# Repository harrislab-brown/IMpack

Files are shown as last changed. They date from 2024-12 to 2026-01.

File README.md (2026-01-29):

# IMpack

<p align="center">
  
</p>

IMpack is a data logging IMU designed for research applications where sampling rate and compactness are paramount. The board costs less than $100 to fabricate and assemble and features an array of MEMS accelerometer chips which allow it to achieve a maximum acceleration measurement range of +/- 400 g, sampling rates up to 26.6 kHz and an angular rate measurement range of +/- 2000 deg/s. Compared to commercial options that use piezoresistive accelerometer elements and complicated analog frontends, the IMpack is very low cost while still achieving good signal-to-noise ratios via its highly selectable measurement range. The IMpack is 38 mm in diameter and approximately 13 mm thick including the single-cell LiPo battery which powers the device. The mass of the PCB itself is 5 grams; including the specified battery, the mass is 9 grams. The battery can be recharged using the micro USB port and the onboard charging circuitry. The microcontroller (STM32F4) gathers data from 3 high performance MEMS IMU chips and logs data to a micro SD card in a plain text CSV format. The parameters for recording including measurement range and sample rate are adjustable via a plain text settings file on the SD card which is used to configure the device on startup. An I2C expansion port allows the IMpack to interface with external sensors, or the synchronization of an array of IMpacks.

# Capabilities

The IMpack can be configured to sample data using any subset of the chips in its sensor array, including all of them at maximum sampling rate simultaneously. All of the chips used measure acceleration in three axes and the LSM6DSO32 contains a gyroscope as well. Sensor components with different strengths are chosen to improve the versatility of the device to different measurement situations. The MEMS IMU parts used and their primary specifications are listed in the following table.

| Sensor | Sample rate (kHz) | Bandwidth (kHz) | Range | Bit depth |
| :---: | :---: | :---: | :---: | :---: |
| IIS3DWB | 26.6 | 6.3 | +/- 16 g | 16 |
| LSM6DSO32 (accel.) | 6.66 | 3.33 | +/- 32 g | 16 |
| LSM6DSO32 (gyro.) | 6.66 | 1.44 | +/- 2000 deg/s | 16 |
| ADXL373 | 5.12 | 2.56 | +/- 400 g | 12 |

The frequency responses of each of 10 IMpack test units are shown in the plots below for data gathered from each IMU chip on the PCB. More details regarding the test setup are available in the accompanying publication (pre-print in the article directory). The raw testing data are available in the data directory.

<p align="center">
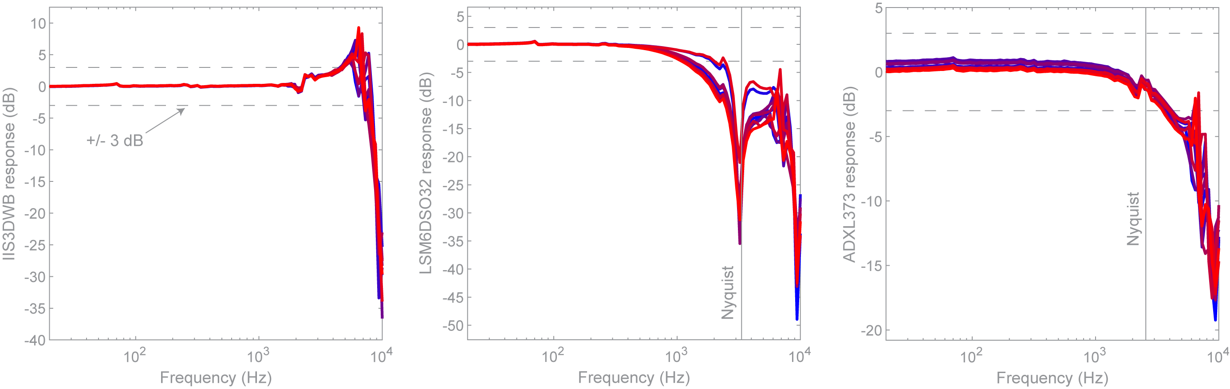
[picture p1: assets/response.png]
  
</p>

# Bill of materials

| Description | Specification |
| :---: | :---: |
| Assembled IMpack PCB |  |
| Mounting fixture or enclosure | Examples in mechanical directory |
| Mounting screws | 4x M2 or #2 cap screws |
| Micro SD card | SanDisk Industrial 8 GB |
| LiPo battery | TinyCircuits ASR00003 |
| Adhesive rubber battery padding | McMaster-Carr 1374N13 |
| Programming cable | Tag-Connect TC2030 |
| Programmer | STLINK-V3MINIE |

# Instructions for use

<p align="center">
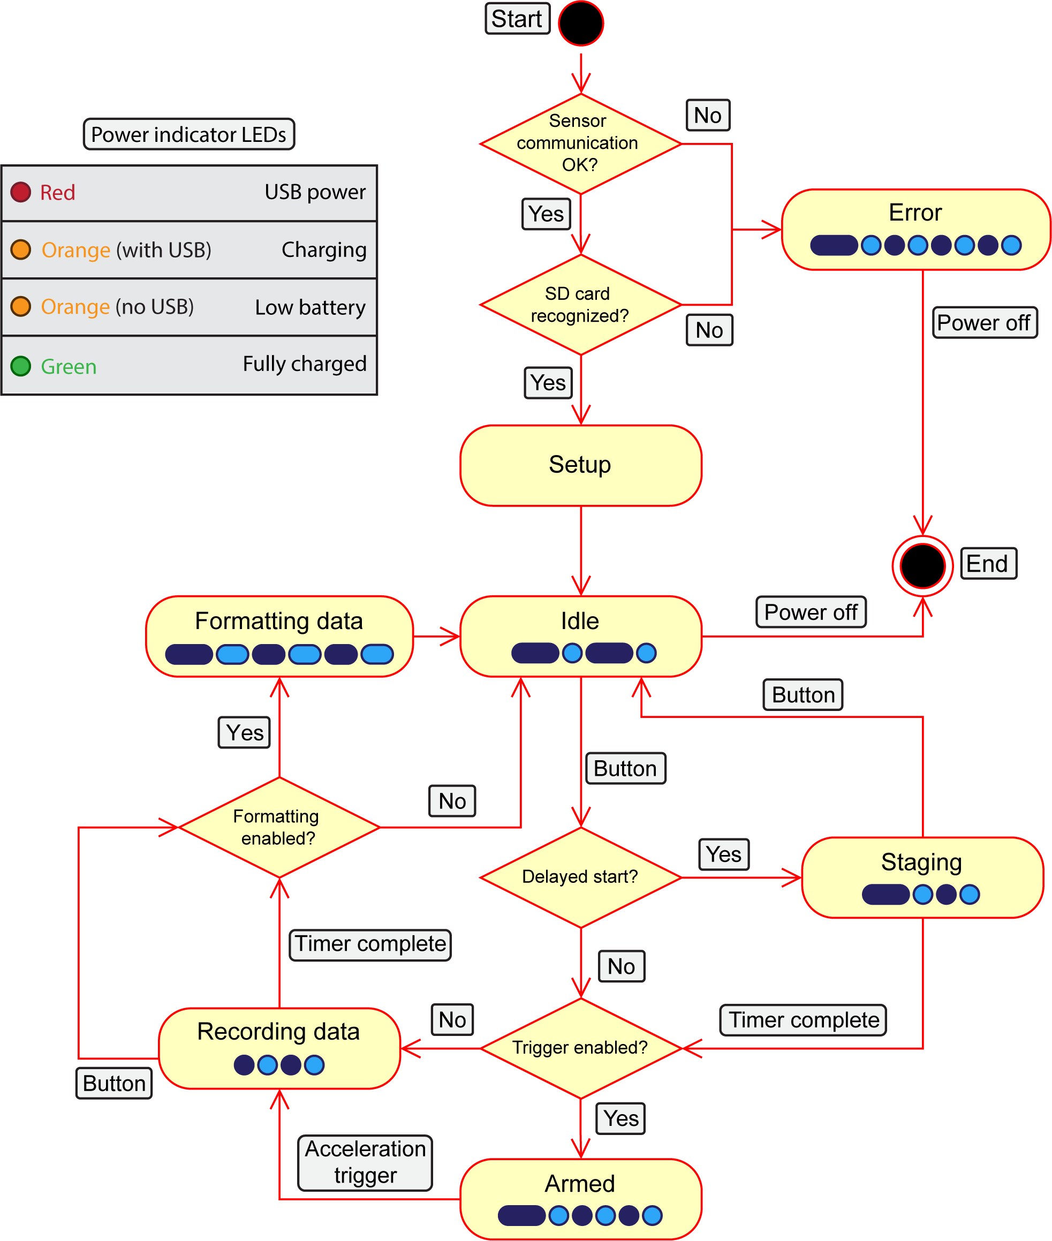
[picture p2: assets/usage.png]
  
</p>

This diagram illustrates the flow of operation of the IMpack. The red, orange and green LEDs are power indicators. The blue LED indicates the state of the device via its periodic blink sequence, where the width of each marker in the diagram indicates the duration of the blink and the light blue color indicates the LED is on. Once the device is powered up and initializes using the settings file on the SD card, pressing the button will begin and end a recording. Recordings can have a delayed start or acceleration trigger, or can stop after a predefined amount of time depending on the configuration as discussed in more detail later.   

## Programming the board

The IMpack is programmed via Serial Wire Debug using an [STLINK-V3MINIE](https://www.mouser.com/ProductDetail/STMicroelectronics/STLINK-V3MINIE?qs=MyNHzdoqoQKcLQe5Jawcgw%3D%3D&mgh=1&utm_id=17222215321&gad_source=1&gclid=Cj0KCQiA3sq6BhD2ARIsAJ8MRwUawTum9u1zJQP-2fxdKjuHkomzrG7uCrwYJbI-F8R0_4U0DyUifOMaAq6kEALw_wcB) debugger and a [Tag-Connect TC2030](https://www.tag-connect.com/product/tc2030-ctx-nl-stdc14-for-use-with-stm32-processors-with-stlink-v3) cable and [retaining clip](https://www.tag-connect.com/product/tc2030-retaining-clip-board-3-pack). We use [STM32CubeIDE](https://www.st.com/en/development-tools/stm32cubeide.html) to compile and launch the project. In the case of a failed flashing that results in an unresponsive microcontroller, the "boot" jumper on the top of the IMpack can be shorted at power up to initialize the microcontroller in boot mode and recover it.

## Charging the battery

The IMpack can be powered from any single-cell lithium polymer battery that can provide at least 150 mA of current and support a 100 mA charge rate. The battery connector is 2-pin JST-SH. We use a [150 mAh battery](https://tinycircuits.com/products/lithium-ion-polymer-battery-3-7v-150mah?srsltid=AfmBOopFKh3iH_07LgFVlMNDD-mnGZ0MBEidQ0zw9-TLOAf2Frq8NPOu) which provides approximately 2 hours of operation on a full charge. The battery polarity is indicated with silkscreen markings near the battery connector. Be sure that your battery matches since there seems to be some variation among different manufacturers.

The IMpack battery can be charged using the micro USB port with the power switch in either the on or off position. The red LED indicates that the IMpack is receiving power over USB. The IMpack can optionally be powered over USB only with no need for a battery. The orange and green LEDs indicate the charge status of the battery. While the USB is plugged in, the orange LED indicates that the battery is charging and the green LED turns on once the battery is fully charged. When operating the device without the USB plugged in, the orange LED will turn on once the battery voltage is low and it needs to be recharged.

## SD card

The IMpack logs data and reads in the recording parameters using a micro SD card. We use an [8 GB SanDisk Industrial](https://www.amazon.com/SanDisk-Industrial-MicroSDHC-SDSDQAF3-008G-I-Everything/dp/B085GL89HQ?th=1) card. The card should be formatted as FAT32. The IMpack will operate in the top-level directory of the card so it is recommended to use an empty card without any important data. 

The IMpack will likely work well with a variety of SD cards but an important factor to note is the write latency of the SD card. This specification is often provided as a generous upper bound so it is difficult to compare the real world performance of different SD cards based on their datasheets. If the real world write latency is too large, some IMU data can be lost during recording. In our testing the IMpack with SanDisk Industrial cards data loss is exceedingly rare.

## Taking a recording

With the IMpack connected to a power source (USB, battery or both), flip the power switch to the on position. The microcontroller will initialize the system and attempt to read in the settings file (more on that later). If the initialization is successful, the blue LED will blink twice. If no settings file is provided or the settings file is formatted incorrectly, the blue LED will blink 4 times. In this case the IMpack will write a correctly formatted default settings file to the card which can subsequently be tweaked by the user to configure the device. The blue LED should then begin flashing once every second, indicating that the device is in the idle state and ready to begin a recording. If instead there is a repeating sequence of 4 blinks, then the IMpack is in an error state (commonly due to a missing SD card).  

When the IMpack is idle, press the button to begin a recording. If a delay is configured, the device will enter the setup state where it waits before recording. A repeating sequence of 2 blue blinks indicates that the IMpack is in the setup state. After the configured delay, the device will enter the armed state if the recording is configured to begin based on an acceleration trigger. A repeating sequence of 3 blinks indicates that the IMpack is in the armed state. Once the acceleration trigger is detected, the device will begin recording, as indicated by rapid blinking of the blue LED. The recording will stop either after the configured recording length, or when the user presses the button again. After the recording, if data formatting is enabled, the device will spend some time formatting the raw sensor data into a plain text CSV file. A sequence of 3 slow blinks will indicate this state. Finally the device will return to the idle state at which point a new recording can be started or the device can be powered off. When the IMpack is not in use, the power switch should be in the off position to avoid draining the battery.

The recording sequence can be configured using the settings file and not all of the aforementioned states will necessarily be seen. For instance, if the delay before the armed state is set to zero and acceleration triggering is disabled, the device will immediately enter the recording state and begin logging data once the button is pressed. Similarly, the formatting state with 3 slow blinks will not be seen if data formatting is disabled, which may be desirable for long recordings at high data rates since the formatting can take a long time. In this case, the recording will be a binary file with the raw sensor data.

## Settings file

The settings.txt file on the SD card is used to configure the IMpack at startup. The sampling parameters for each IMU channel can be configured, as well as the overall recording parameters such as whether to wait for an acceleration trigger or whether to perform plain text formatting of the data file. An annotated example of the default settings file is shown below describing each of the parameters and their allowed values. If a valid settings file is not found on startup, the IMpack will generate a default one on the SD card - this is the recommended way to get started with the configuration.

```
LSM6DSx_accel_enabled = 1  # enable or disable each measurement channel with values 1 or 0
LSM6DSx_accel_odr_hz = 6660  # allowed values: 13, 26, 52, 104, 208, 416, 833, 1660, 3330, 6660
LSM6DSx_accel_range_g = 32  # allowed values: 4, 8, 16, 32
LSM6DSx_accel_lpf = 2  # setting for the low pass filter, 2 means bandwidth = ODR / 2 and so on (same meaning for other the other accelerometers), allowed values: 2, 4, 10, 20, 45, 100, 200, 400, 800
LSM6DSx_accel_offset_x_mg = 0  # these are DC offsets in milli-g, signed integer
LSM6DSx_accel_offset_y_mg = 0
LSM6DSx_accel_offset_z_mg = 0

LSM6DSx_gyro_enabled = 1
LSM6DSx_gyro_odr_hz = 6660  # allowed values: 13, 26, 52, 104, 208, 416, 833, 1660, 3330, 6660
LSM6DSx_gyro_range_dps = 2000  # allowed values: 125, 250, 500, 1000, 2000
LSM6DSx_gyro_lpf = 3  # this is the bit value that is put in the chip register, consult table 60 in LSM6DSO32 data sheet, allowed values: 0, 1, 2, 3, 4, 5, 6, 7

IIS3DWB_accel_enabled = 1
IIS3DWB_accel_range_g = 16  # allowed values: 2, 4, 8, 16
IIS3DWB_accel_lpf = 4  # allowed values: 4, 10, 20, 45, 100, 200, 400, 800
IIS3DWB_accel_offset_x_mg = 0
IIS3DWB_accel_offset_y_mg = 0
IIS3DWB_accel_offset_z_mg = 0

ADXL37x_accel_enabled = 1
ADXL37x_accel_odr_hz = 5120  # allowed values: 320, 640, 1280, 2560, 5120
ADXL37x_accel_lpf = 2  # allowed values: 2, 4, 8, 16, 32
ADXL37x_accel_offset_x_mg = 0
ADXL37x_accel_offset_y_mg = 0
ADXL37x_accel_offset_z_mg = 0

delay_before_armed_ms = 0  # how long to remain in the staging state in ms
recording_length_ms = 5000  # how long to record for in ms
data_formatting_enabled = 1  # if enabled, will create CSV files after each recording
accel_trigger_enabled = 0  # once armed, the recording will start based on an acceleration trigger if enabled
accel_trigger_on_any_axis = 0  # trigger if any axis exceeds the threshold if 1, else if 0 looks only for specific axis
accel_trigger_axis = 2  # 0, 1, 2 for x, y, z, axis selection to trigger from
accel_trigger_level_mg = 500  # level of the trigger in units of milli-g
accel_trigger_rising_edge = 0  # select whether to trigger on rising or falling edge
```

## Data format

When plain text data formatting is enabled, the IMpack will create a separate CSV file for each active channel from the recording. The columns for time stamps and axis measurements are labeled with units, so interpreting the file should be straightforward. The binary data files consist of sequences of data points which each consist of 12 bytes. Each data point contains the unsigned 32 bit time stamp in microseconds, 3 axes of signed 16 bit acceleration/angular rate data, and finally unsigned 16 bit data type tag to indicate which channel produced the data. Example scripts for parsing the binary data in MATLAB and Python are provided in the examples directory. 

# Hardware design

<p align="center">
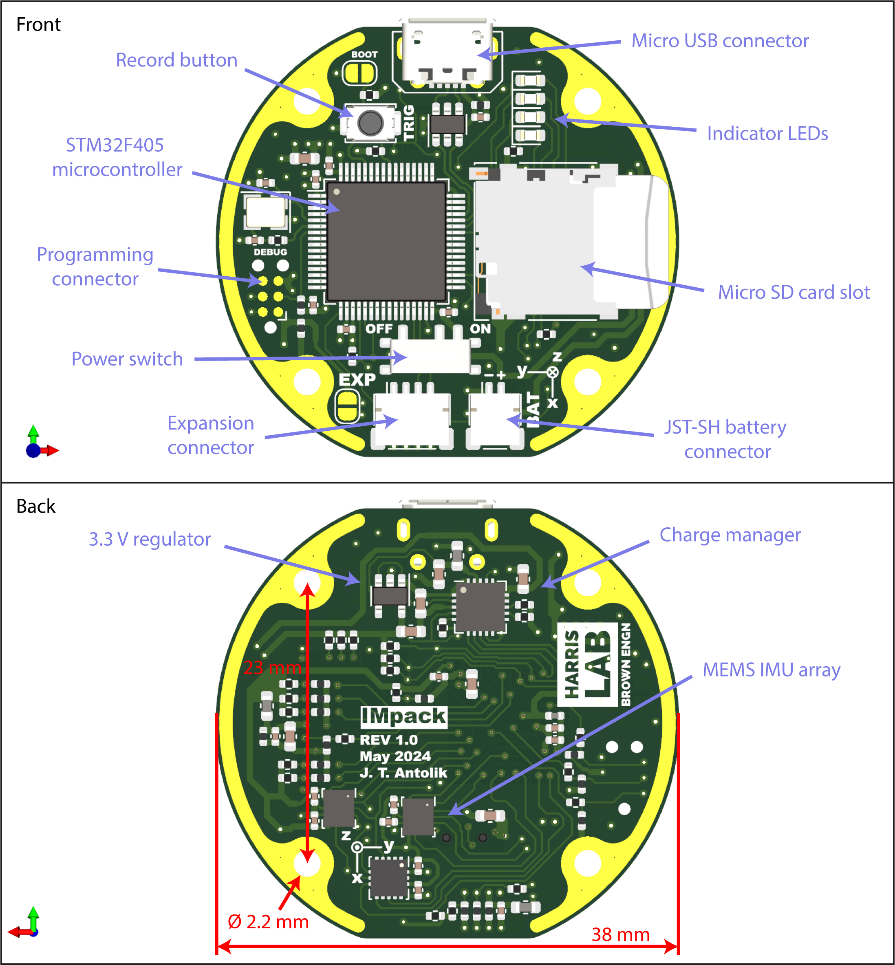
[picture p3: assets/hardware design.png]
  
</p>

The board schematics, production files and KiCad 8 design files are available in the hardware directory. An enclosure or fixture is required to mount the IMpack depending on the application, which could be 3D printed or machined from metal in more stringent testing setups. Design files for the mechanical assemblies into which we mount the IMpack are available in the mechanical directory as examples. In our use case, we apply an adhesive rubber pad to the battery which allows it to be firmly clamped into the battery pocket as the IMpack mounting screws are tightened. The PCB is 4 layers with double sided assembly. The main components and their functions are listed below. A spreadsheet with all of the required components is available under hardware/production.

  - STM32F405 microcontroller (we use SDIO, SPI, NVIC, USB-FS, SWD, I2C hardware)
  - MCP73871 battery charge controller
  - TLV70033 LDO regulator
  - DM3D-SF micro SD card holder (most compact I could find)
  - IIS3DWB super high speed accelerometer with +/- 16 g range
  - ADXL373 high-g range accelerometer
  - LSM6DSO32 combined gyroscope and accelerometer with +/- 32 g range, low cost and widely available fallback option

We ordered 20 fully assembled IMpack units in calendar year 2024 to be manufactured by JLCPCB in batches of 5 or 10. The total cost per board ended up between 60 and 80 USD. A large contributor to the cost is the high performance accelerometer chips IIS3DWB and ADXL373 which typically cost 20 USD per chip in low quanitites. The board could be manufactured with the LSM6DSO32 as the only IMU chip, saving approximately 40 USD per unit, without otherwise compromising the functionality. 

# Firmware design

The source code for the IMpack is available as an STM32CubeIDE project in the firmware directory. The IMpack firmware is written in C and developed using the toolchain provided with STM32CubeIDE version 1.16.0 along with ST's Hardware Abstraction Layer library provided in the STM32Cube FW_F4 V1.28.1 firmware package. The IMpack firmware uses an interrupt based scheme to retrieve data from the IMU chips resulting in minimum latency in which the MCU listens to the data ready pin from each chip and initiates the SPI data read on the appropriate edges of the data pin signal. The SPI read subroutine uses direct register manipulation for improved speed. Each data packet is tagged with a time stamp and an identifier for which chip it came from and inserted into a large double buffer in RAM. The buffer is written to a file on the SD card in binary format periodically as each half of the buffer is filled. Finally, at the end of the recording, the binary data file is read back and converted into a CSV text file on the SD card for more convenient processing by the user. A big challenge is the SD card write latency (up to 250 ms latency according to the data sheet for the SanDisk Industrial card used). Data from the IMU chips needs to be double buffered so we can put new data from the sensors in one half while the other half is being written to the file. This means we would have to store 500 ms worth of data in memory to guarantee no data loss. At such high data rates, this is not feasible without using additional memory chips or a larger MCU. In practice, the actual latency of the SD card we selected is much lower so we don't lose data, but this is something to be aware of if a different SD card is used. Data loss can be easily detected by calculating the interval between successive data point time stamps and comparing with the expected sampling period based on the configuration.

# License

IMpack is licensed under the CC BY-SA 4.0 Creative Commons license.

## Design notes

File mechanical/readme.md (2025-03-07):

## IMpack mechanical designs

This directory contains step files and native Fusion 360 design files for the IMpack itself as well as the fixtures we designed to hold it during testing which can serve as an example for user applications. The shaker mount was used to attach the IMpack to the mechanical shaker for frequency response testing. The threaded mount was used to hold the IMpack in the submerisble water impactor which produced the water entry data. The mounting geometry for the IMpack itself and the battery pocket are the same in both designs and should be replicated in a machined aluminum part if relying on our frequency response data. Note that the IMpack is designed for the plated ring around the outside perimeter of the board's bottom face to act as the mechanical mounting surface. For less sensitive applications or preliminary testing 3D printed parts will likely work fine.

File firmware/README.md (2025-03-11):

# Firmware

This directory contains the STM32CubeIDE project for the IMpack. The project specific header files can be found under firmware/IMpack/Core/Inc and the implementation files under firmware/IMpack/Core/Src. The main application code is contained in app.c following a roughly object-oriented design paradigm where the objects are defined in the corresponding commented header files.

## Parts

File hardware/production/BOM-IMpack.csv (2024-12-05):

Comment | Designator | Footprint | LCSC | Quantity
100R | FB201,FB501,FB701 | L_0603_1608Metric | C1002 | 3
TLV70033_SOT23-5 | U202 | SOT-23-5 | C11337 | 1
16MHz | Y301 | Crystal_SMD_3225-4Pin_3.2x2.5mm | C13738 | 1
10n | C310 | C_0402_1005Metric | C15195 | 1
100n | C302,C304,C306,C307,C308,C312,C401,C502,C601,C602,C603,C604,C605,C606,C701 | C_0402_1005Metric | C1525 | 15
12p | C311,C313 | C_0402_1005Metric | C1547 | 2
STM32F405RGT6 | U301 | LQFP-64_10x10mm_P0.5mm | C15742 | 1
JST_SH_BAT | J201 | JST_SH_SM02B-SRSS-TB_1x02-1MP_P1.00mm_Horizontal | C160402 | 1
JST_SH_EXPANSION | J701 | JST_SH_SM04B-SRSS-TB_1x04-1MP_P1.00mm_Horizontal | C160404 | 1
LSM6DSO32TR | U601 | LGA-14_3x2.5mm_P0.5mm_LayoutBorder3x4y | C1864162 | 1
4u7 | C202,C203,C204 | C_0603_1608Metric | C19666 | 3
10u | C201,C301,C501 | C_0603_1608Metric | C19702 | 3
BUTTON | SW301 | SW_Push_SPST_NO_Alps_SKRK | C202388 | 1
RED | D201 | LED_0603_1608Metric | C2286 | 1
2u2 | C303,C305 | C_0603_1608Metric | C23630 | 2
22 | R305,R306,R307,R501 | R_0402_1005Metric | C25092 | 4
47 | R304 | R_0402_1005Metric | C25118 | 1
510 | R209 | R_0402_1005Metric | C25123 | 1
100k | R202 | R_0402_1005Metric | C25741 | 1
10k | R201,R203,R204,R205,R206,R302,R303,R701,R702 | R_0402_1005Metric | C25744 | 9
47k | R502,R503,R504,R505,R506,R507,R601,R602,R603 | R_0402_1005Metric | C25792 | 9
1k5 | R207,R208,R301 | R_0402_1005Metric | C25867 | 3
39n | L301 | L_0402_1005Metric | C26443 | 1
USBLC6-2SC6 | U401 | SOT-23-6 | C2827654 | 1
SW_ON_OFF | SW201 | MSS12C02LS-BB2.0 | C3008585 | 1
RCLAMP0521P-N | D302,D303,D304,D305,D306,D401,D501,D502,D503,D504,D505,D506,D507,D508,D701,D702,D703 | D_0402_1005Metric | C316043 | 17
ADXL37x | U602 | Analog_LGA-16_3.25x3mm_P0.5mm_LayoutBorder3x5y | C3216386 | 1
USB_B_Micro | J401 | MicroXNJ | C404969 | 1
MCP73871 | U201 | QFN-20-1EP_4x4mm_P0.5mm_EP2.5x2.5mm | C511310 | 1
1u | C309 | C_0402_1005Metric | C52923 | 1
IIS3DWBTR | U603 | LGA-14_3x2.5mm_P0.5mm_LayoutBorder3x4y | C717702 | 1
DM3D-SF | J501 | microSD_HC_Hirose_DM3D-SF | C719027 | 1
GREEN | D203 | LED_0603_1608Metric | C84264 | 1
BLUE | D301 | LED_0603_1608Metric | C84266 | 1
ORANGE | D202 | LED_0603_1608Metric | C84269 | 1

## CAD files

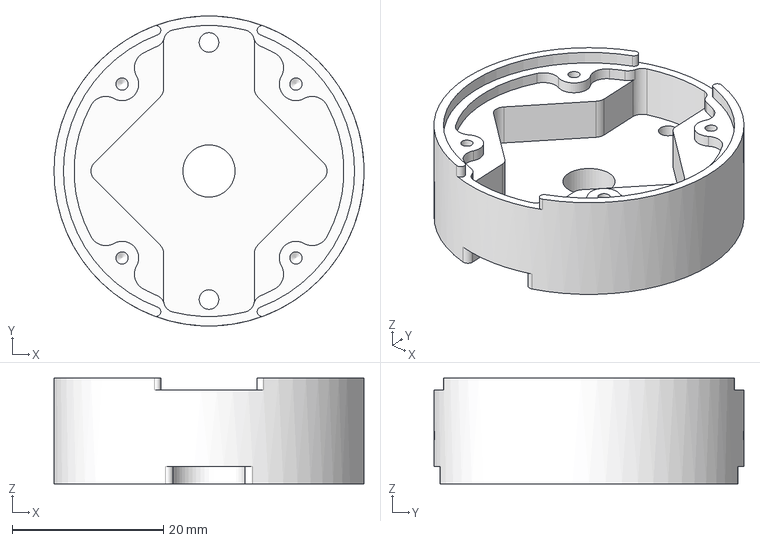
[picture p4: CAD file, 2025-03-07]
mechanical/IMpack shaker mount.step
41.0 x 41.0 x 14.0 mm

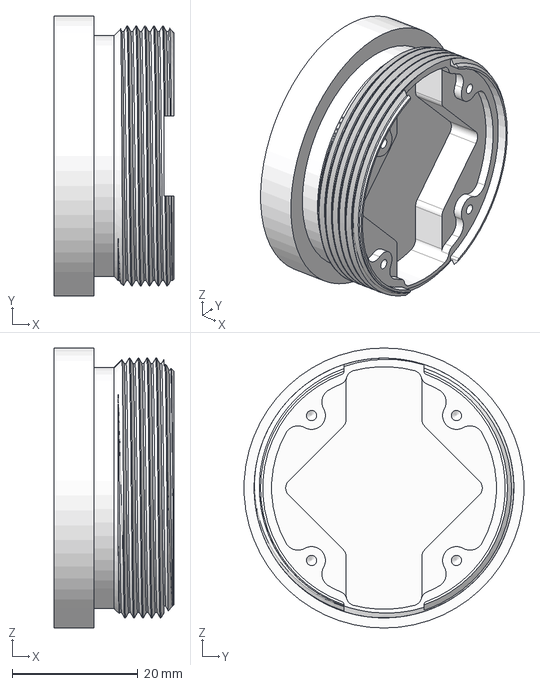
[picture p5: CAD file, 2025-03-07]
mechanical/IMpack threaded mount.step
19.0 x 44.4 x 44.4 mm

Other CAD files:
mechanical/IMpack shaker mount.f3z
mechanical/IMpack threaded mount.f3d

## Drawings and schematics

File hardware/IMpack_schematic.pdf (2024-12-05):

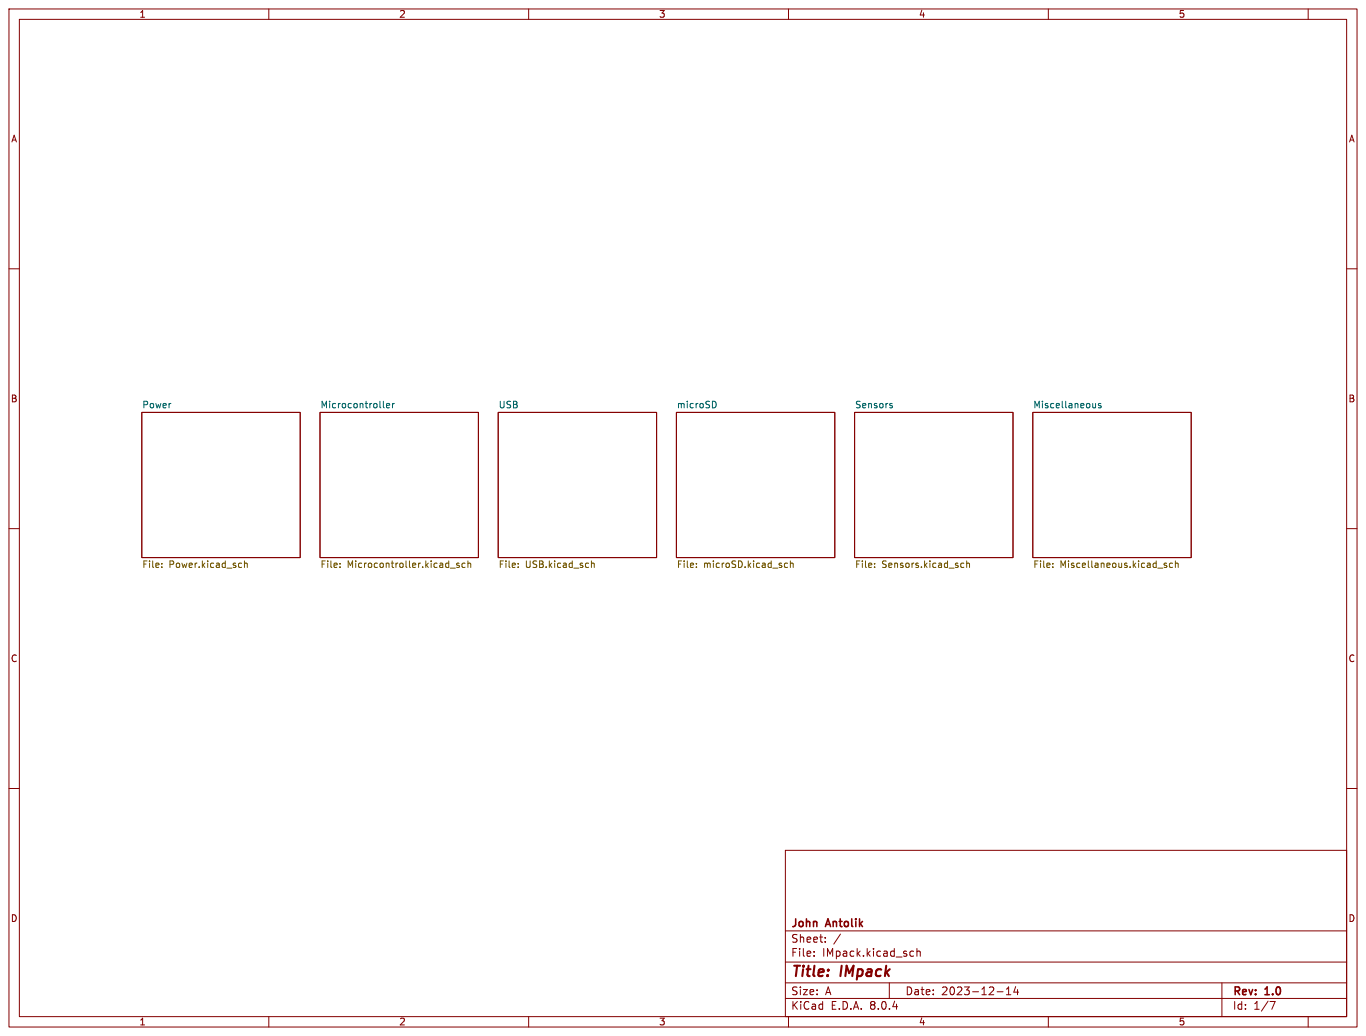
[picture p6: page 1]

File: IMpack.kicad_sch Sheet: / John Antolik

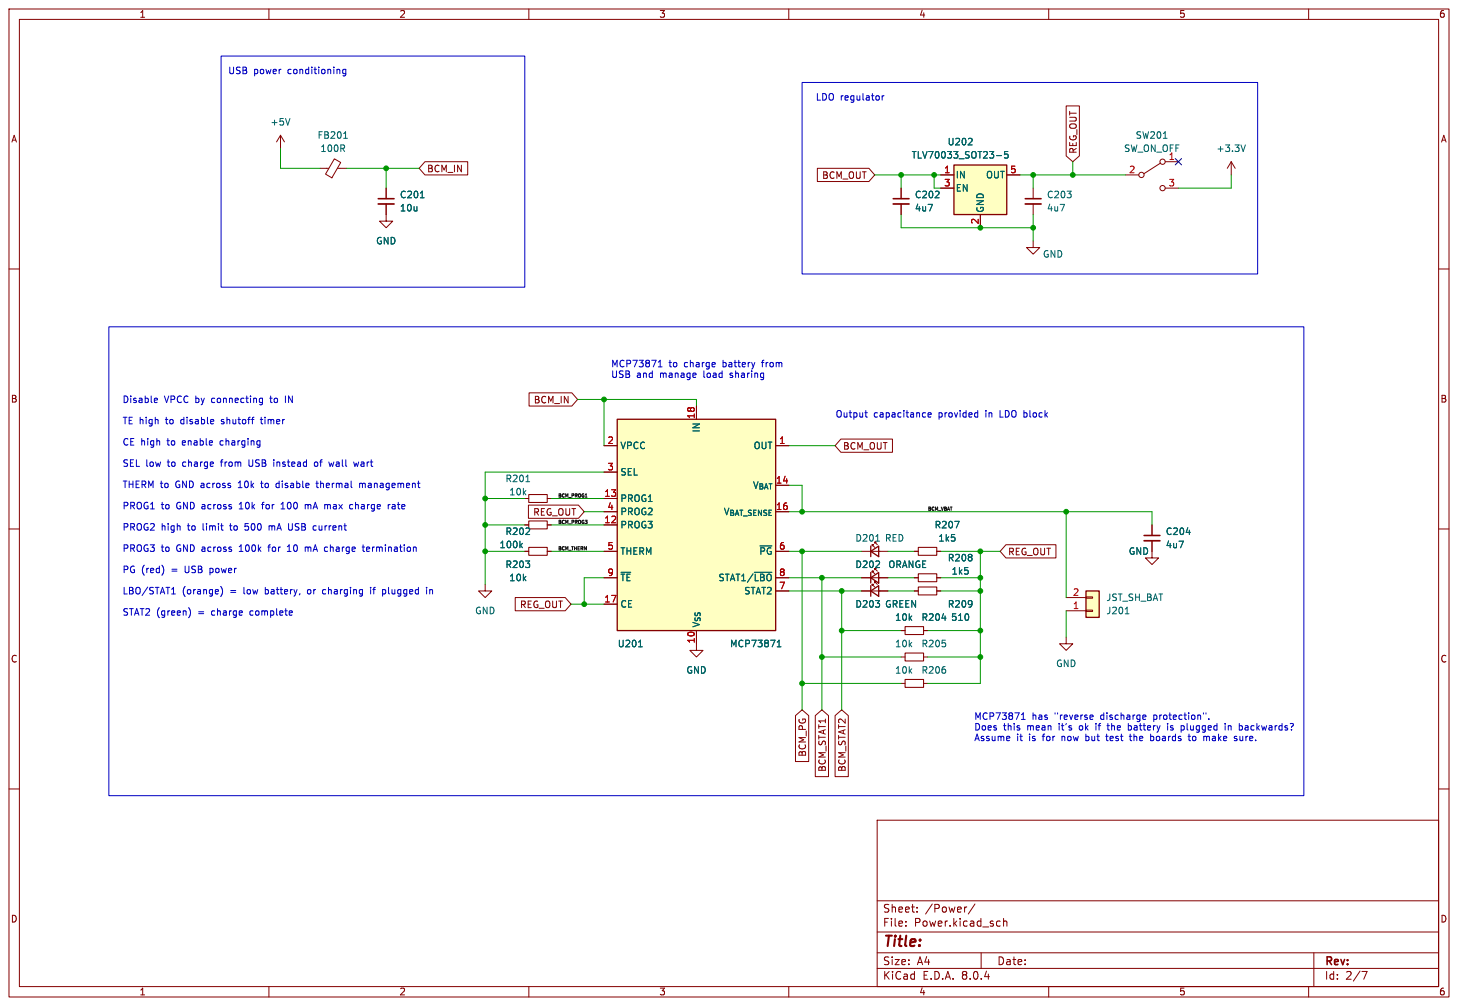
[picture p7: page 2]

Id: 2/7 Title: File: Power.kicad_sch Sheet: /Power/ R208

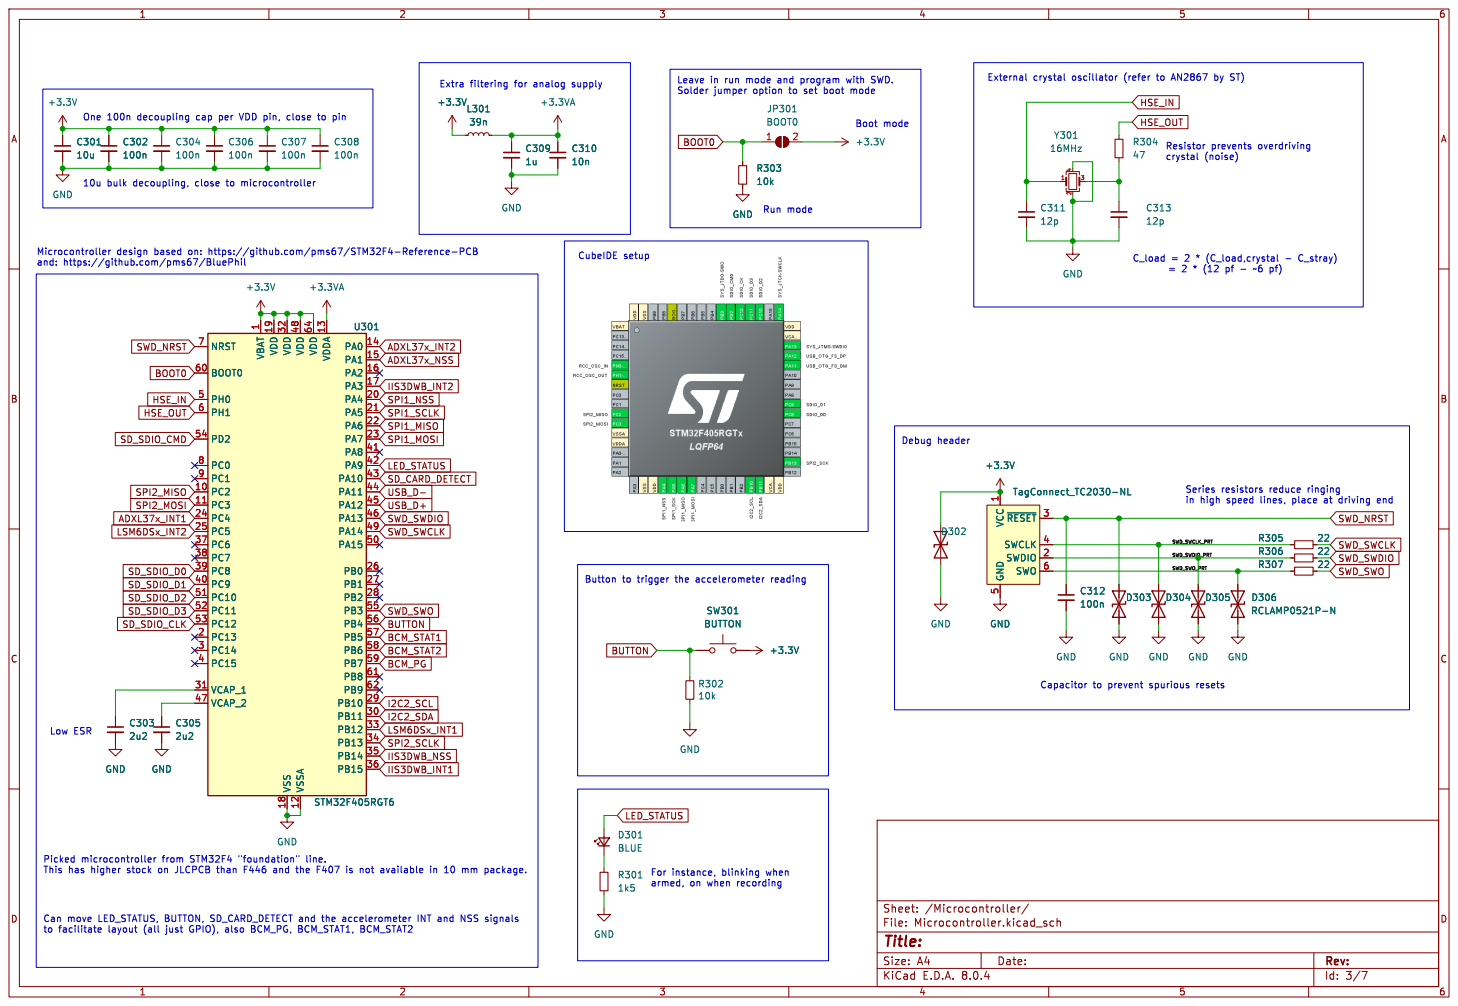
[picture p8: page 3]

1 PC2 10 PC3 11 VSSA 12 VDDA 13 PA0 14 PA1 15 PA2 16 PA3 17 VSS 18 VDD 19 PC13 2 PA4 20 PA5 21 PA6 22 PA7 23 PC4 24 PC5 25 PB0 26 PB1 27 PB2 28 PB10 29 PC14 3 PB11 30 VCAP_1 31 VDD 32 PB12 33 PB13 34 PB14 35 PB15 36 PC6 37 PC7 38 PC8 39 PC15 4 PC9 40 PA8 41 PA9 42 PA10 43 PA11 44 PA12 45 PA13 46 VCAP_2 47 VDD 48 PA14 49 PH0 5 PA15 50 PC10 51 PC11 52 PC12 53 PD2 54 PB3 55 PB4 56 PB5 57 PB6 58 PB7 59 PH1 6 BOOT0 60 PB8 61 PB9 62 VDD 64 NRST 7 PC0 8 PC1 9 U301 STM32F405RGT6 GND GND GND GND

1 PC2 10 PC3 11 VSSA 12 VDDA 13 PA0 14 PA1 15 PA2 16 PA3 17 VSS 18 VDD 19 PC13 2 PA4 20 PA5 21 PA6 22 PA7 23 PC4 24 PC5 25 PB0 26 PB1 27 PB2 28 PB10 29 PC14 3 PB11 30 VCAP_1 31 VDD 32 PB12 33 PB13 34 PB14 35 PB15 36 PC6 37 PC7 38 PC8 39 PC15 4 PC9 40 PA8 41 PA9 42 PA10 43 PA11 44 PA12 45 PA13 46 VCAP_2 47 VDD 48 PA14 49 PH0 5 PA15 50 PC10 51 PC11 52 PC12 53 PD2 54 PB3 55 PB4 56 PB5 57 PB6 58 PB7 59 PH1 6 BOOT0 60 PB8 61 PB9 62 VDD 64 NRST 7 PC0 8 PC1 9 C305

1 SWDIO 2 ~{RESET}3 SWCLK 4 GND

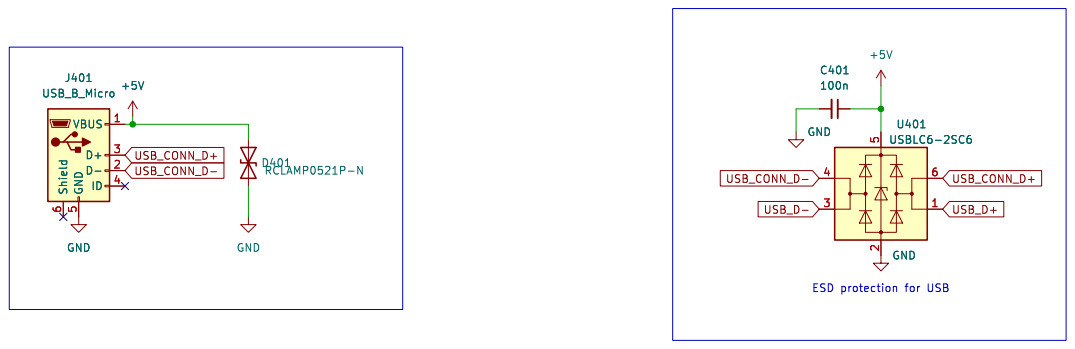
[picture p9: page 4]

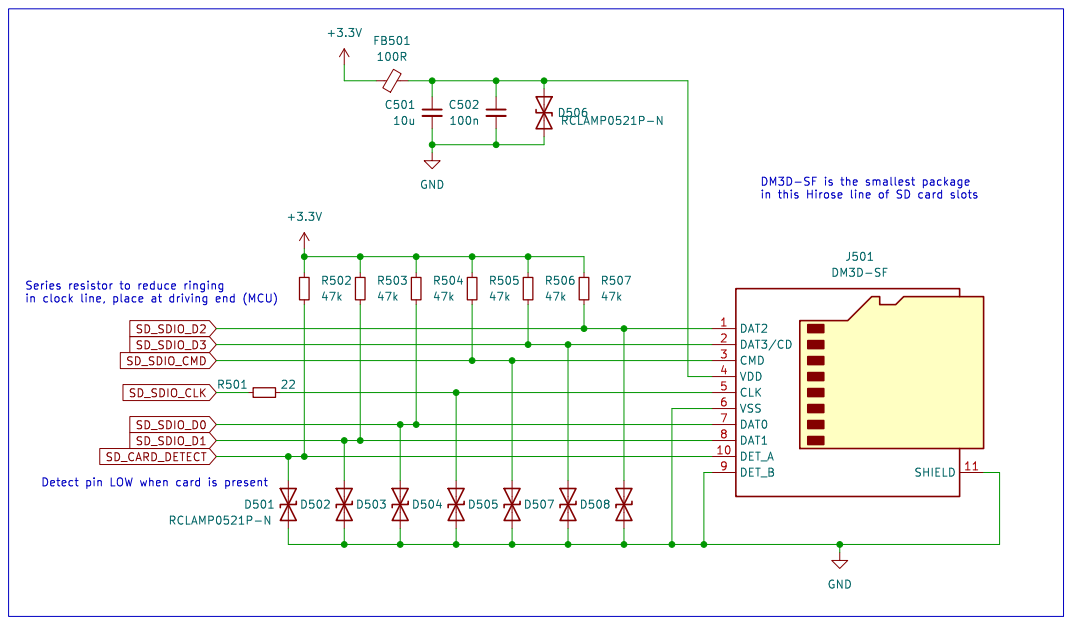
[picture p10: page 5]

in this Hirose line of SD card slots

Id: 5/7 Title: File: microSD.kicad_sch Sheet: /microSD/

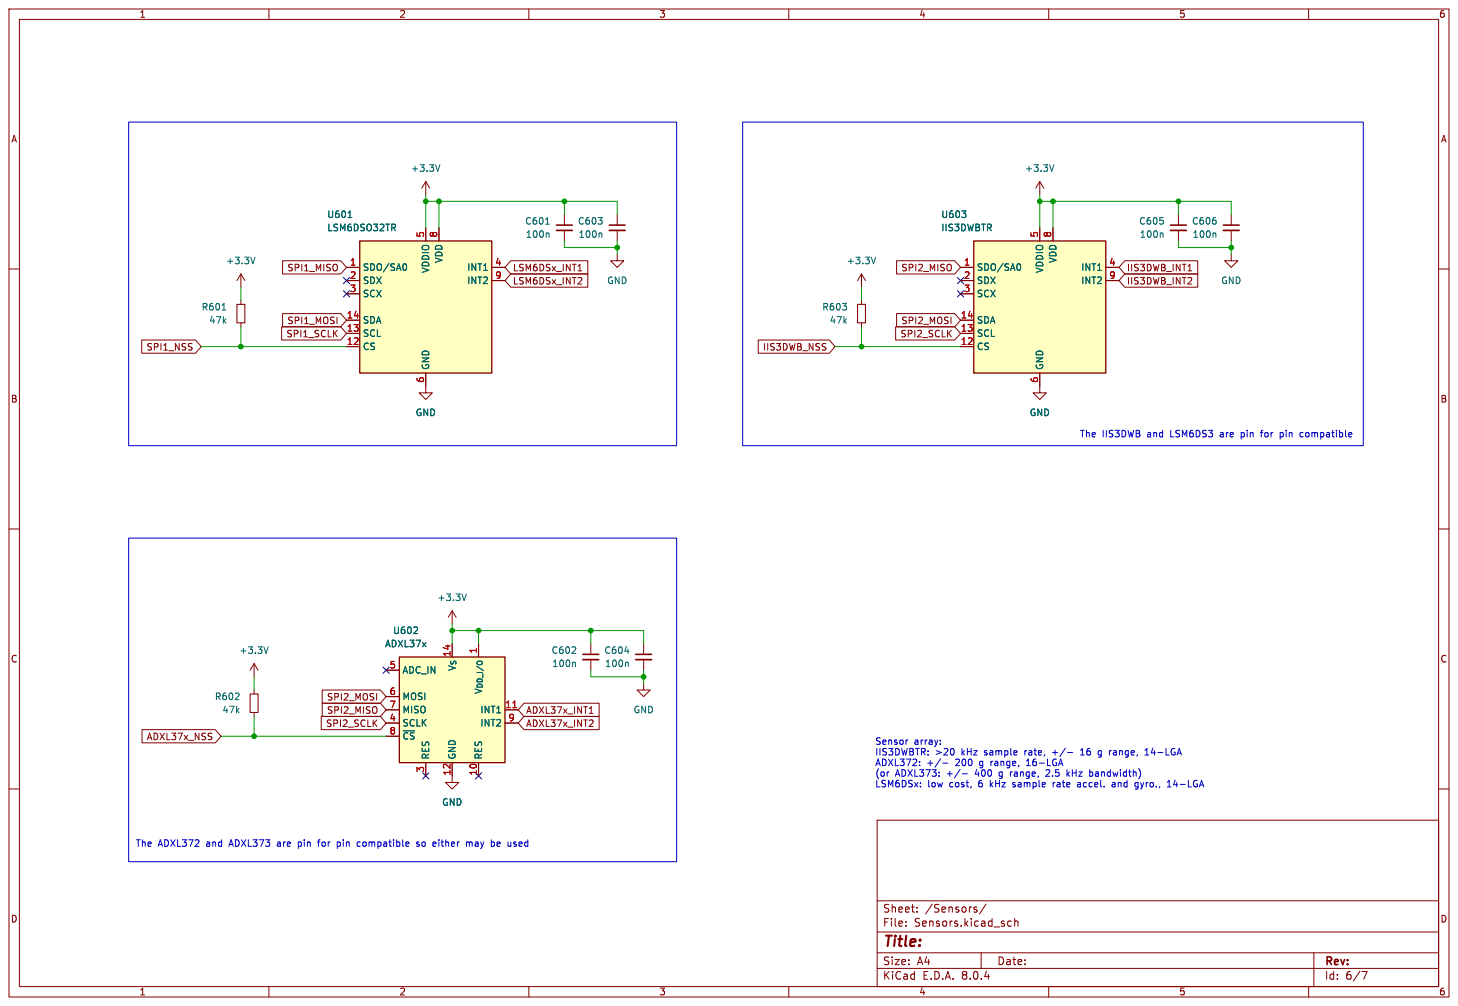
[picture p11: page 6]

The IIS3DWB and LSM6DS3 are pin for pin compatible Sensor array:

3 SCLK 4 ADC_IN 5 MOSI 6 MISO 7 ~{CS} 8

Id: 6/7 Title: File: Sensors.kicad_sch Sheet: /Sensors/

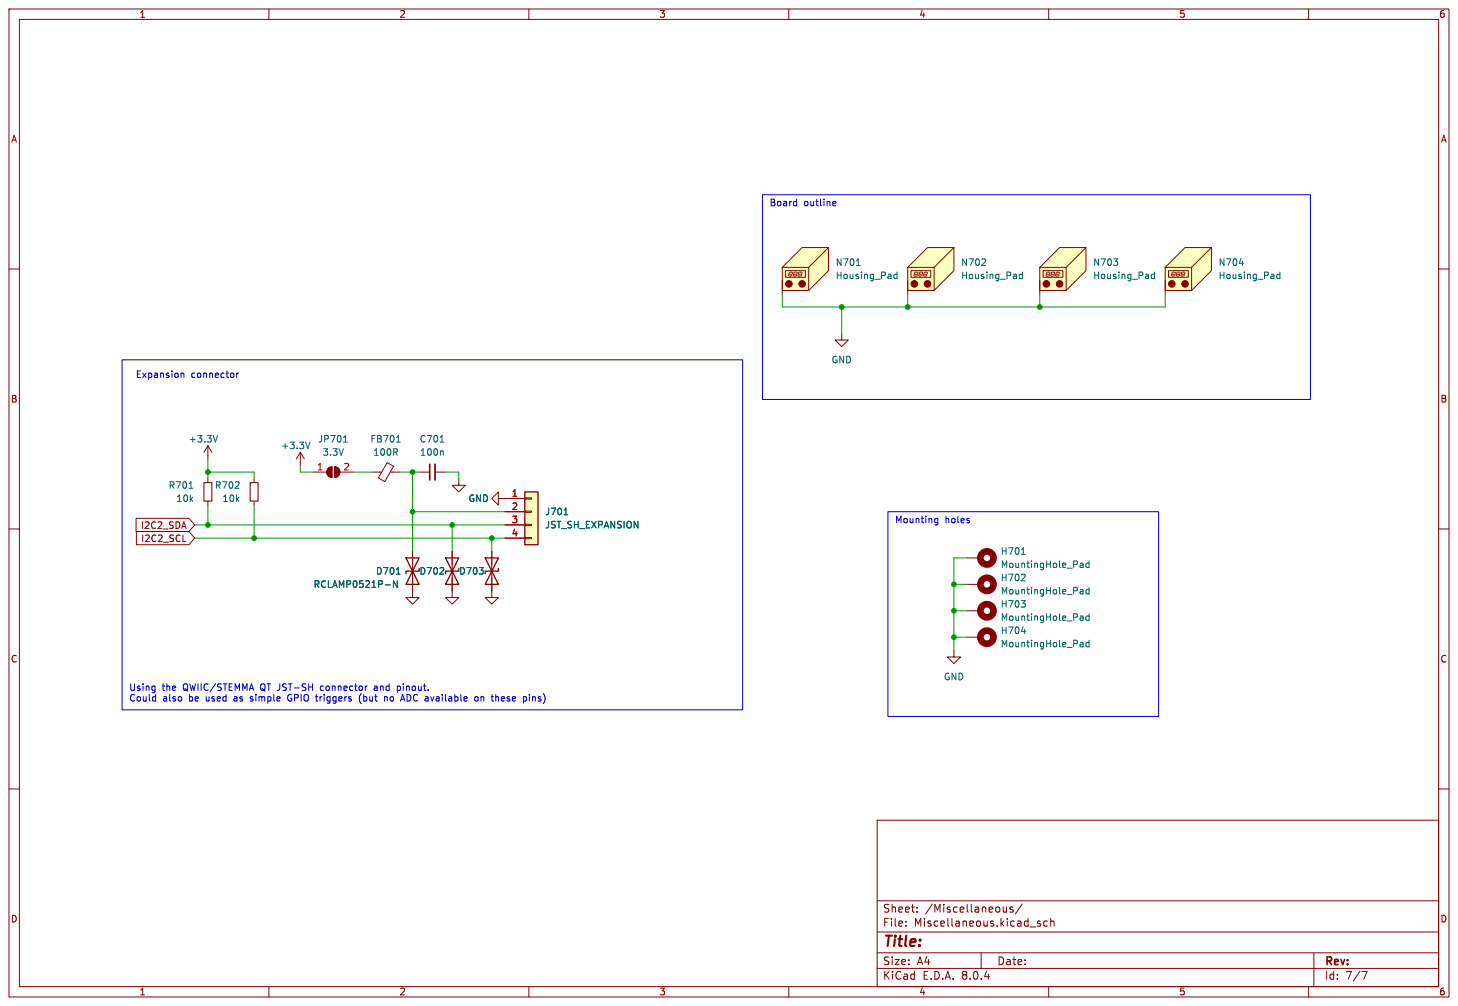
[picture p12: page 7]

Id: 7/7 Title: File: Miscellaneous.kicad_sch Sheet: /Miscellaneous/H702 MountingHole_Pad N702 Housing_Pad GND

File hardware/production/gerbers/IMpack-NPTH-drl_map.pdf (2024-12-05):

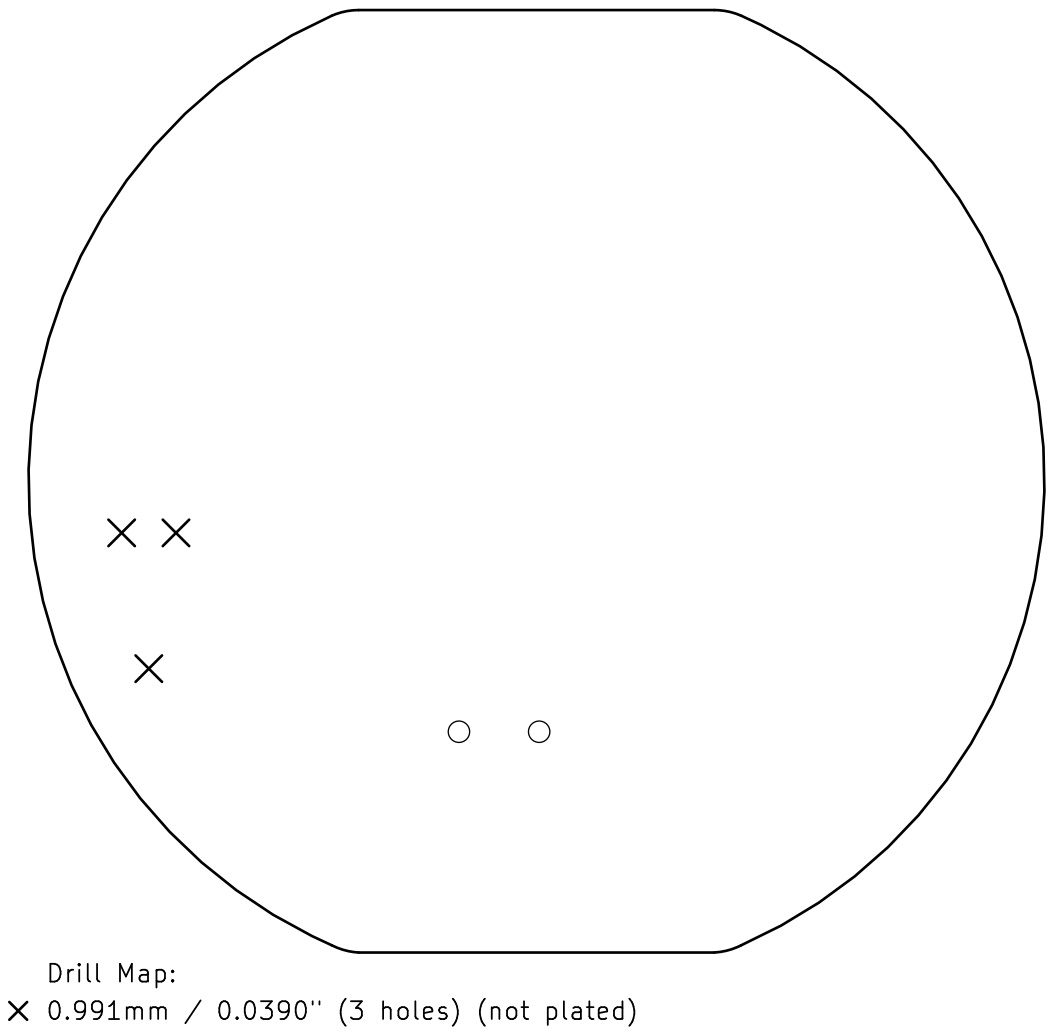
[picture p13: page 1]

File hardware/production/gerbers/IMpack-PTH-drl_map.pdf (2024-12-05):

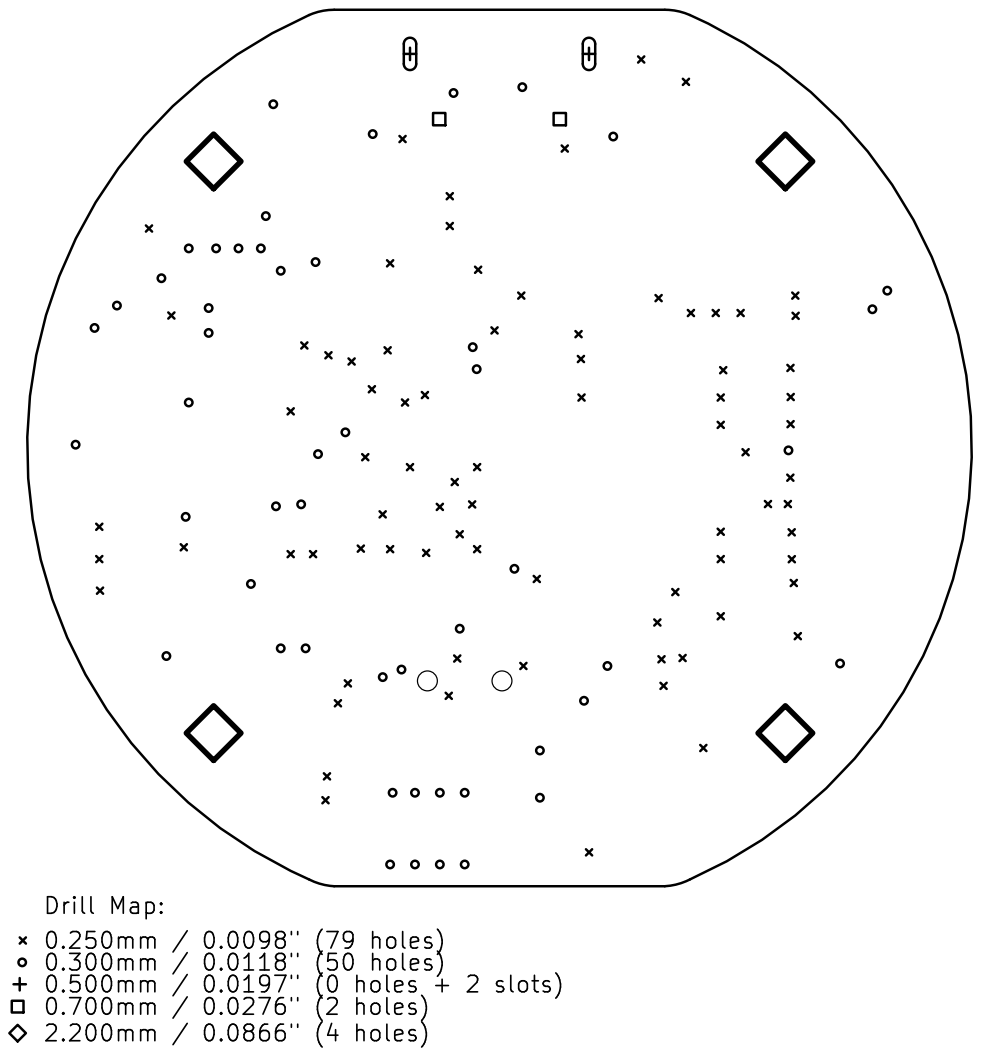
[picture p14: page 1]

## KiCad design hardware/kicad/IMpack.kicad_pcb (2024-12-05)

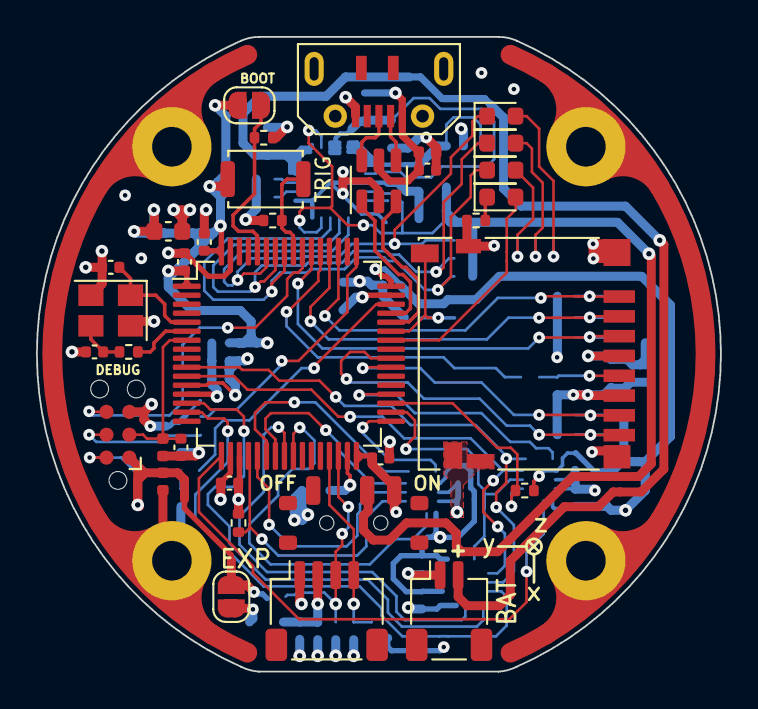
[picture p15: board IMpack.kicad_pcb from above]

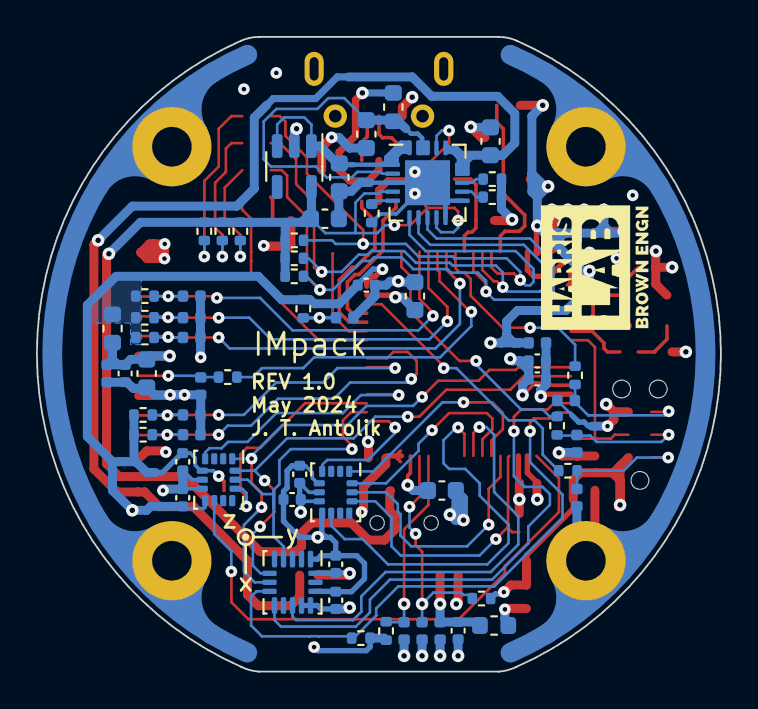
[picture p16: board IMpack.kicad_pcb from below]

Board: 4 copper layers, 38.0 x 35.3 mm, 105 parts (65 on the bottom side), 65 nets.

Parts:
C201, C301, C501: 10u; C_0603_1608Metric
C202, C203, C204: 4u7; C_0603_1608Metric
C302, C304, C306, C307, C308, C312, C401, C502, C601, C602, C603, C604, C605, C606, C701: 100n; C_0402_1005Metric
C303, C305: 2u2; C_0603_1608Metric
C309: 1u; C_0402_1005Metric
C310: 10n; C_0402_1005Metric
C311, C313: 12p; C_0402_1005Metric
D201: RED; LED_0603_1608Metric
D202: ORANGE; LED_0603_1608Metric
D203: GREEN; LED_0603_1608Metric
D301: BLUE; LED_0603_1608Metric
D302, D303, D304, D305, D306, D401, D501, D502, D503, D504, D505, D506, D507, D508, D701, D702, D703: RCLAMP0521P-N; D_0402_1005Metric
FB201, FB501, FB701: 100R; L_0603_1608Metric
H701, H702, H703, H704: MountingHole_Pad; MountingHole_2.2mm_M2_Pad
J201: JST_SH_BAT; JST_SH_SM02B-SRSS-TB_1x02-1MP_P1.00mm_Horizontal
J301: TagConnect_TC2030-NL; Tag-Connect_TC2030-IDC-NL_2x03_P1.27mm_Vertical
J401: USB_B_Micro; MicroXNJ
J501: DM3D-SF; microSD_HC_Hirose_DM3D-SF
J701: JST_SH_EXPANSION; JST_SH_SM04B-SRSS-TB_1x04-1MP_P1.00mm_Horizontal
JP301: BOOT0; SolderJumper-2_P1.3mm_Open_RoundedPad1.0x1.5mm
JP701: 3.3V; SolderJumper-2_P1.3mm_Open_RoundedPad1.0x1.5mm
L301: 39n; L_0402_1005Metric
N701, N702, N703, N704: Housing_Pad; Board_Outline
R201, R203, R204, R205, R206, R302, R303, R701, R702: 10k; R_0402_1005Metric
R202: 100k; R_0402_1005Metric
R207, R208, R301: 1k5; R_0402_1005Metric
R209: 510; R_0402_1005Metric
R304: 47; R_0402_1005Metric
R305, R306, R307, R501: 22; R_0402_1005Metric
R502, R503, R504, R505, R506, R507, R601, R602, R603: 47k; R_0402_1005Metric
SW201: SW_ON_OFF; MSS12C02LS-BB2.0
SW301: BUTTON; SW_Push_SPST_NO_Alps_SKRK
U201: MCP73871; QFN-20-1EP_4x4mm_P0.5mm_EP2.5x2.5mm
U202: TLV70033_SOT23-5; SOT-23-5
U301: STM32F405RGT6; LQFP-64_10x10mm_P0.5mm
U401: USBLC6-2SC6; SOT-23-6
U601: LSM6DSO32TR; LGA-14_3x2.5mm_P0.5mm_LayoutBorder3x4y
U602: ADXL37x; Analog_LGA-16_3.25x3mm_P0.5mm_LayoutBorder3x5y
U603: IIS3DWBTR; LGA-14_3x2.5mm_P0.5mm_LayoutBorder3x4y
Y301: 16MHz; Crystal_SMD_3225-4Pin_3.2x2.5mm

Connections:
+3.3V: C301.1, C302.1, C304.1, C306.1, C307.1, C308.1, C601.1, C602.1, C603.1, C604.1, C605.1, C606.1, D302.1 (A1), FB501.1, J301.1 (VCC), JP301.2 (B), JP701.1 (A), L301.1, R502.1, R503.1, R504.1, R505.1, R506.1, R507.1, R601.1, R602.1, R603.1, R701.1, R702.1, SW201.3 (C), SW301.2, U301.1 (VBAT), U301.19 (VDD), U301.32 (VDD), U301.48 (VDD), U301.64 (VDD), U601.5 (VDDIO), U601.8 (VDD), U602.1 (V_{DD_I/O}), U602.14 (V_{S}), U603.5 (VDDIO), U603.8 (VDD)
+3.3VA: C309.1, C310.1, L301.2, U301.13 (VDDA)
+5V: C401.1, D401.1 (A1), FB201.1, J401.1 (VBUS), U401.5 (VBUS)
/Microcontroller/SWD_SWCLK_PRT: D304.1 (A1), J301.4 (SWCLK), R305.2
/Microcontroller/SWD_SWDIO_PRT: D305.1 (A1), J301.2 (SWDIO), R306.2
/Microcontroller/SWD_SWO_PRT: D306.1 (A1), J301.6 (SWO), R307.2
/Power/BCM_PROG1: R201.2, U201.13 (PROG1)
/Power/BCM_PROG3: R202.2, U201.12 (PROG3)
/Power/BCM_THERM: R203.2, U201.5 (THERM)
/Power/BCM_VBAT: C204.1, J201.2, U201.14 (V_{BAT}), U201.15 (V_{BAT}), U201.16 (V_{BAT_SENSE})
ADXL37x_INT1: U301.24 (PC4), U602.11 (INT1)
ADXL37x_INT2: U301.14 (PA0), U602.9 (INT2)
ADXL37x_NSS: R602.2, U301.15 (PA1), U602.8 (~CS)
BCM_IN: C201.1, FB201.2, U201.2 (VPCC), U201.18 (IN), U201.19 (IN)
BCM_OUT: C202.1, U201.1 (OUT), U201.20 (OUT), U202.1 (IN), U202.3 (EN)
BCM_PG: D201.1 (K), R206.2, U201.6 (~PG), U301.59 (PB7)
BCM_STAT1: D202.1 (K), R205.2, U201.8 (STAT1/~LBO), U301.57 (PB5)
BCM_STAT2: D203.1 (K), R204.2, U201.7 (STAT2), U301.58 (PB6)
BOOT0: JP301.1 (A), R303.1, U301.60 (BOOT0)
BUTTON: R302.1, SW301.1, U301.56 (PB4)
GND: C201.2, C202.2, C203.2, C204.2, C301.2, C302.2, C303.2, C304.2, C305.2, C306.2, C307.2, C308.2, C309.2, C310.2, C311.2, C312.2, C313.2, C401.2, C501.2, C502.2, C601.2, C602.2, C603.2, C604.2, C605.2, C606.2, C701.2, D302.2 (A2), D303.2 (A2), D304.2 (A2), D305.2 (A2), D306.2 (A2), D401.2 (A2), D501.2 (A2), D502.2 (A2), D503.2 (A2), D504.2 (A2), D505.2 (A2), D506.2 (A2), D507.2 (A2), D508.2 (A2), D701.2 (A2), D702.2 (A2), D703.2 (A2), H701.1, H702.1, H703.1, H704.1, J201.1, J301.5 (GND), J401.5 (GND), J501.6 (VSS), J501.9 (DET_B), J501.11 (SHIELD), J701.1, N701.1 (PAD), N702.1 (PAD), N703.1 (PAD), N704.1 (PAD), R201.1, R202.1, R203.1, R301.2, R302.2, R303.2, U201.3 (SEL), U201.10 (V_{SS}), U201.11 (V_{SS}), U201.21 (V_{SS}), U202.2 (GND), U301.12 (VSSA), U301.18 (VSS), U301.63 (VSS), U401.2 (GND), U601.6 (GND), U601.7 (GND), U602.12 (GND), U602.13 (GND), U602.16 (GND), U603.6 (GND), U603.7 (GND), Y301.2, Y301.4
HSE_IN: C311.1, U301.5 (PH0), Y301.1
HSE_OUT: R304.1, U301.6 (PH1)
I2C2_SCL: D703.1 (A1), J701.4, R702.2, U301.29 (PB10)
I2C2_SDA: D702.1 (A1), J701.3, R701.2, U301.30 (PB11)
IIS3DWB_INT1: U301.36 (PB15), U603.4 (INT1)
IIS3DWB_INT2: U301.17 (PA3), U603.9 (INT2)
IIS3DWB_NSS: R603.2, U301.35 (PB14), U603.12 (CS)
LED_STATUS: D301.2 (A), U301.42 (PA9)
LSM6DSx_INT1: U301.33 (PB12), U601.4 (INT1)
LSM6DSx_INT2: U301.25 (PC5), U601.9 (INT2)
unnamed: C313.1, R304.2, Y301.3
unnamed: D201.2 (A), R207.1
unnamed: D202.2 (A), R208.1
unnamed: D203.2 (A), R209.1
unnamed: D301.1 (K), R301.1
unnamed: D504.1 (A1), J501.5 (CLK), R501.1
unnamed: C501.1, C502.1, D506.1 (A1), FB501.2, J501.4 (VDD)
unnamed: C701.1, D701.1 (A1), FB701.2, J701.2
unnamed: FB701.1, JP701.2 (B)
unnamed: C303.1, U301.31 (VCAP_1)
unnamed: C305.1, U301.47 (VCAP_2)
REG_OUT: C203.1, R204.1, R205.1, R206.1, R207.2, R208.2, R209.2, SW201.2 (B), U201.4 (PROG2), U201.9 (~TE), U201.17 (CE), U202.5 (OUT)
SD_CARD_DETECT: D501.1 (A1), J501.10 (DET_A), R502.2, U301.43 (PA10)
SD_SDIO_CLK: R501.2, U301.53 (PC12)
SD_SDIO_CMD: D505.1 (A1), J501.3 (CMD), R505.2, U301.54 (PD2)
SD_SDIO_D0: D503.1 (A1), J501.7 (DAT0), R504.2, U301.39 (PC8)
SD_SDIO_D1: D502.1 (A1), J501.8 (DAT1), R503.2, U301.40 (PC9)
SD_SDIO_D2: D508.1 (A1), J501.1 (DAT2), R507.2, U301.51 (PC10)
SD_SDIO_D3: D507.1 (A1), J501.2 (DAT3/CD), R506.2, U301.52 (PC11)
SPI1_MISO: U301.22 (PA6), U601.1 (SDO/SA0)
SPI1_MOSI: U301.23 (PA7), U601.14 (SDA)
SPI1_NSS: R601.2, U301.20 (PA4), U601.12 (CS)
SPI1_SCLK: U301.21 (PA5), U601.13 (SCL)
SPI2_MISO: U301.10 (PC2), U602.7 (MISO), U603.1 (SDO/SA0)
SPI2_MOSI: U301.11 (PC3), U602.6 (MOSI), U603.14 (SDA)
SPI2_SCLK: U301.34 (PB13), U602.4 (SCLK), U603.13 (SCL)
SWD_NRST: C312.1, D303.1 (A1), J301.3 (~RESET), U301.7 (NRST)
SWD_SWCLK: R305.1, U301.49 (PA14)
SWD_SWDIO: R306.1, U301.46 (PA13)
SWD_SWO: R307.1, U301.55 (PB3)
USB_CONN_D+: J401.3 (D+), U401.6 (I/O1)
USB_CONN_D-: J401.2 (D-), U401.4 (I/O2)
USB_D+: U301.45 (PA12), U401.1 (I/O1)
USB_D-: U301.44 (PA11), U401.3 (I/O2)

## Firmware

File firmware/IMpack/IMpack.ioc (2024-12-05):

#MicroXplorer Configuration settings - do not modify
CAD.formats=
CAD.pinconfig=
CAD.provider=
Dma.Request0=SDIO_RX
Dma.Request1=SDIO_TX
Dma.RequestsNb=2
Dma.SDIO_RX.0.Direction=DMA_PERIPH_TO_MEMORY
Dma.SDIO_RX.0.FIFOMode=DMA_FIFOMODE_ENABLE
Dma.SDIO_RX.0.FIFOThreshold=DMA_FIFO_THRESHOLD_FULL
Dma.SDIO_RX.0.Instance=DMA2_Stream3
Dma.SDIO_RX.0.MemBurst=DMA_MBURST_INC4
Dma.SDIO_RX.0.MemDataAlignment=DMA_MDATAALIGN_WORD
Dma.SDIO_RX.0.MemInc=DMA_MINC_ENABLE
Dma.SDIO_RX.0.Mode=DMA_PFCTRL
Dma.SDIO_RX.0.PeriphBurst=DMA_PBURST_INC4
Dma.SDIO_RX.0.PeriphDataAlignment=DMA_PDATAALIGN_WORD
Dma.SDIO_RX.0.PeriphInc=DMA_PINC_DISABLE
Dma.SDIO_RX.0.Priority=DMA_PRIORITY_MEDIUM
Dma.SDIO_RX.0.RequestParameters=Instance,Direction,PeriphInc,MemInc,PeriphDataAlignment,MemDataAlignment,Mode,Priority,FIFOMode,FIFOThreshold,MemBurst,PeriphBurst
Dma.SDIO_TX.1.Direction=DMA_MEMORY_TO_PERIPH
Dma.SDIO_TX.1.FIFOMode=DMA_FIFOMODE_ENABLE
Dma.SDIO_TX.1.FIFOThreshold=DMA_FIFO_THRESHOLD_FULL
Dma.SDIO_TX.1.Instance=DMA2_Stream6
Dma.SDIO_TX.1.MemBurst=DMA_MBURST_INC4
Dma.SDIO_TX.1.MemDataAlignment=DMA_MDATAALIGN_WORD
Dma.SDIO_TX.1.MemInc=DMA_MINC_ENABLE
Dma.SDIO_TX.1.Mode=DMA_PFCTRL
Dma.SDIO_TX.1.PeriphBurst=DMA_PBURST_INC4
Dma.SDIO_TX.1.PeriphDataAlignment=DMA_PDATAALIGN_WORD
Dma.SDIO_TX.1.PeriphInc=DMA_PINC_DISABLE
Dma.SDIO_TX.1.Priority=DMA_PRIORITY_MEDIUM
Dma.SDIO_TX.1.RequestParameters=Instance,Direction,PeriphInc,MemInc,PeriphDataAlignment,MemDataAlignment,Mode,Priority,FIFOMode,FIFOThreshold,MemBurst,PeriphBurst
FATFS.BSP.number=1
FATFS.IPParameters=USE_DMA_CODE_SD,_FS_LOCK
FATFS.USE_DMA_CODE_SD=1
FATFS._FS_LOCK=0
FATFS0.BSP.STBoard=false
FATFS0.BSP.api=Unknown
FATFS0.BSP.component=
FATFS0.BSP.condition=
FATFS0.BSP.instance=PA10
FATFS0.BSP.ip=GPIO
FATFS0.BSP.mode=Input
FATFS0.BSP.name=Detect_SDIO
FATFS0.BSP.semaphore=
FATFS0.BSP.solution=PA10
File.Version=6
GPIO.groupedBy=Group By Peripherals
KeepUserPlacement=false
Mcu.CPN=STM32F405RGT6
Mcu.Family=STM32F4
Mcu.IP0=DMA
Mcu.IP1=FATFS
Mcu.IP10=TIM3
Mcu.IP11=USB_OTG_FS
Mcu.IP2=I2C2
Mcu.IP3=NVIC
Mcu.IP4=RCC
Mcu.IP5=SDIO
Mcu.IP6=SPI1
Mcu.IP7=SPI2
Mcu.IP8=SYS
Mcu.IP9=TIM2
Mcu.IPNb=12
Mcu.Name=STM32F405RGTx
Mcu.Package=LQFP64
Mcu.Pin0=PH0-OSC_IN
Mcu.Pin1=PH1-OSC_OUT
Mcu.Pin10=PA7
Mcu.Pin11=PC4
Mcu.Pin12=PC5
Mcu.Pin13=PB10
Mcu.Pin14=PB11
Mcu.Pin15=PB12
Mcu.Pin16=PB13
Mcu.Pin17=PB14
Mcu.Pin18=PB15
Mcu.Pin19=PC8
Mcu.Pin2=PC2
Mcu.Pin20=PC9
Mcu.Pin21=PA9
Mcu.Pin22=PA10
Mcu.Pin23=PA11
Mcu.Pin24=PA12
Mcu.Pin25=PA13
Mcu.Pin26=PA14
Mcu.Pin27=PC10
Mcu.Pin28=PC11
Mcu.Pin29=PC12
Mcu.Pin3=PC3
Mcu.Pin30=PD2
Mcu.Pin31=PB3
Mcu.Pin32=PB4
Mcu.Pin33=VP_FATFS_VS_SDIO
Mcu.Pin34=VP_SYS_VS_Systick
Mcu.Pin35=VP_TIM2_VS_ClockSourceINT
Mcu.Pin36=VP_TIM3_VS_ClockSourceINT
Mcu.Pin4=PA0-WKUP
Mcu.Pin5=PA1
Mcu.Pin6=PA3
Mcu.Pin7=PA4
Mcu.Pin8=PA5
Mcu.Pin9=PA6
Mcu.PinsNb=37
Mcu.ThirdPartyNb=0
Mcu.UserConstants=
Mcu.UserName=STM32F405RGTx
MxCube.Version=6.12.0
MxDb.Version=DB.6.0.120
NVIC.BusFault_IRQn=true\:1\:1\:true\:false\:true\:false\:false\:false
NVIC.DMA2_Stream3_IRQn=true\:2\:2\:true\:false\:true\:true\:true\:true
NVIC.DMA2_Stream6_IRQn=true\:2\:2\:true\:false\:true\:true\:true\:true
NVIC.DebugMonitor_IRQn=true\:1\:1\:true\:false\:true\:false\:false\:false
NVIC.EXTI15_10_IRQn=true\:0\:0\:true\:false\:true\:true\:true\:true
NVIC.EXTI4_IRQn=true\:0\:0\:true\:false\:true\:true\:true\:true
NVIC.EXTI9_5_IRQn=true\:0\:0\:true\:false\:true\:true\:true\:true
NVIC.ForceEnableDMAVector=false
NVIC.HardFault_IRQn=true\:0\:0\:false\:false\:true\:false\:false\:false
NVIC.MemoryManagement_IRQn=true\:1\:1\:true\:false\:true\:false\:false\:false
NVIC.NonMaskableInt_IRQn=true\:0\:0\:false\:false\:true\:false\:false\:false
NVIC.PendSV_IRQn=true\:1\:1\:true\:false\:true\:false\:false\:false
NVIC.PriorityGroup=NVIC_PRIORITYGROUP_2
NVIC.SDIO_IRQn=true\:2\:2\:true\:false\:true\:true\:true\:true
NVIC.SVCall_IRQn=true\:1\:1\:true\:false\:true\:false\:false\:false
NVIC.SysTick_IRQn=true\:1\:1\:true\:false\:true\:false\:true\:false
NVIC.TIM3_IRQn=true\:2\:2\:true\:false\:true\:true\:true\:true
NVIC.UsageFault_IRQn=true\:1\:1\:true\:false\:true\:false\:false\:false
PA0-WKUP.GPIOParameters=GPIO_Label
PA0-WKUP.GPIO_Label=ADXL37x_INT2
PA0-WKUP.Locked=true
PA0-WKUP.Signal=GPXTI0
PA1.GPIOParameters=GPIO_Speed,PinState,GPIO_Label
PA1.GPIO_Label=ADXL37x_NSS
PA1.GPIO_Speed=GPIO_SPEED_FREQ_VERY_HIGH
PA1.Locked=true
PA1.PinState=GPIO_PIN_SET
PA1.Signal=GPIO_Output
PA10.GPIOParameters=GPIO_Label
PA10.GPIO_Label=SD_CARD_DETECT
PA10.Locked=true
PA10.Signal=GPIO_Input
PA11.Mode=Device_Only
PA11.Signal=USB_OTG_FS_DM
PA12.Mode=Device_Only
PA12.Signal=USB_OTG_FS_DP
PA13.Mode=Trace_Asynchronous_SW
PA13.Signal=SYS_JTMS-SWDIO
PA14.Mode=Trace_Asynchronous_SW
PA14.Signal=SYS_JTCK-SWCLK
PA3.GPIOParameters=GPIO_Label
PA3.GPIO_Label=IIS3DWB_INT2
PA3.Locked=true
PA3.Signal=GPXTI3
PA4.GPIOParameters=GPIO_Speed,PinState,GPIO_Label
PA4.GPIO_Label=SPI1_NSS
PA4.GPIO_Speed=GPIO_SPEED_FREQ_VERY_HIGH
PA4.Locked=true
PA4.PinState=GPIO_PIN_SET
PA4.Signal=GPIO_Output
PA5.Mode=Full_Duplex_Master
PA5.Signal=SPI1_SCK
PA6.Mode=Full_Duplex_Master
PA6.Signal=SPI1_MISO
PA7.Mode=Full_Duplex_Master
PA7.Signal=SPI1_MOSI
PA9.GPIOParameters=PinState,GPIO_Label
PA9.GPIO_Label=LED_STATUS
PA9.Locked=true
PA9.PinState=GPIO_PIN_RESET
PA9.Signal=GPIO_Output
PB10.GPIOParameters=GPIO_Pu
PB10.GPIO_Pu=GPIO_NOPULL
PB10.Mode=I2C
PB10.Signal=I2C2_SCL
PB11.GPIOParameters=GPIO_Pu
PB11.GPIO_Pu=GPIO_NOPULL
PB11.Mode=I2C
PB11.Signal=I2C2_SDA
PB12.GPIOParameters=GPIO_Label
PB12.GPIO_Label=LSM6DSx_INT1
PB12.Locked=true
PB12.Signal=GPXTI12
PB13.Locked=true
PB13.Mode=Full_Duplex_Master
PB13.Signal=SPI2_SCK
PB14.GPIOParameters=GPIO_Speed,PinState,GPIO_Label
PB14.GPIO_Label=IIS3DWB_NSS
PB14.GPIO_Speed=GPIO_SPEED_FREQ_VERY_HIGH
PB14.Locked=true
PB14.PinState=GPIO_PIN_SET
PB14.Signal=GPIO_Output
PB15.GPIOParameters=GPIO_Label
PB15.GPIO_Label=IIS3DWB_INT1
PB15.Locked=true
PB15.Signal=GPXTI15
PB3.Mode=Trace_Asynchronous_SW
PB3.Signal=SYS_JTDO-SWO
PB4.GPIOParameters=GPIO_Label
PB4.GPIO_Label=BUTTON
PB4.Locked=true
PB4.Signal=GPIO_Input
PC10.Locked=true
PC10.Signal=SDIO_D2
PC11.Locked=true
PC11.Signal=SDIO_D3
PC12.GPIOParameters=GPIO_PuPd
PC12.GPIO_PuPd=GPIO_NOPULL
PC12.Mode=SD_1_bit
PC12.Signal=SDIO_CK
PC2.Mode=Full_Duplex_Master
PC2.Signal=SPI2_MISO
PC3.Mode=Full_Duplex_Master
PC3.Signal=SPI2_MOSI
PC4.GPIOParameters=GPIO_Label
PC4.GPIO_Label=ADXL37x_INT1
PC4.Locked=true
PC4.Signal=GPXTI4
PC5.GPIOParameters=GPIO_Label
PC5.GPIO_Label=LSM6DSx_INT2
PC5.Locked=true
PC5.Signal=GPXTI5
PC8.GPIOParameters=GPIO_PuPd
PC8.GPIO_PuPd=GPIO_NOPULL
PC8.Mode=SD_1_bit
PC8.Signal=SDIO_D0
PC9.Locked=true
PC9.Signal=SDIO_D1
PD2.GPIOParameters=GPIO_PuPd
PD2.GPIO_PuPd=GPIO_NOPULL
PD2.Mode=SD_1_bit
PD2.Signal=SDIO_CMD
PH0-OSC_IN.Mode=HSE-External-Oscillator
PH0-OSC_IN.Signal=RCC_OSC_IN
PH1-OSC_OUT.Mode=HSE-External-Oscillator
PH1-OSC_OUT.Signal=RCC_OSC_OUT
PinOutPanel.RotationAngle=0
ProjectManager.AskForMigrate=true
ProjectManager.BackupPrevious=false
ProjectManager.CompilerOptimize=6
ProjectManager.ComputerToolchain=false
ProjectManager.CoupleFile=false
ProjectManager.CustomerFirmwarePackage=
ProjectManager.DefaultFWLocation=true
ProjectManager.DeletePrevious=true
ProjectManager.DeviceId=STM32F405RGTx
ProjectManager.FirmwarePackage=STM32Cube FW_F4 V1.28.1
ProjectManager.FreePins=false
ProjectManager.HalAssertFull=false
ProjectManager.HeapSize=0x800
ProjectManager.KeepUserCode=true
ProjectManager.LastFirmware=true
ProjectManager.LibraryCopy=1
ProjectManager.MainLocation=Core/Src
ProjectManager.NoMain=false
ProjectManager.PreviousToolchain=
ProjectManager.ProjectBuild=false
ProjectManager.ProjectFileName=IMpack.ioc
ProjectManager.ProjectName=IMpack
ProjectManager.ProjectStructure=
ProjectManager.RegisterCallBack=
ProjectManager.StackSize=0x1600
ProjectManager.TargetToolchain=STM32CubeIDE
ProjectManager.ToolChainLocation=
ProjectManager.UAScriptAfterPath=
ProjectManager.UAScriptBeforePath=
ProjectManager.UnderRoot=true
ProjectManager.functionlistsort=1-SystemClock_Config-RCC-false-HAL-false,2-MX_GPIO_Init-GPIO-false-HAL-true,3-MX_DMA_Init-DMA-false-HAL-true,4-MX_SPI1_Init-SPI1-false-HAL-true,5-MX_SDIO_SD_Init-SDIO-false-HAL-true,6-MX_FATFS_Init-FATFS-false-HAL-false,7-MX_SPI2_Init-SPI2-false-HAL-true,8-MX_TIM2_Init-TIM2-false-HAL-true,9-MX_I2C2_Init-I2C2-false-HAL-true,10-MX_TIM3_Init-TIM3-false-HAL-true,11-MX_USB_OTG_FS_PCD_Init-USB_OTG_FS-false-HAL-true
RCC.48MHZClocksFreq_Value=48000000
RCC.AHBFreq_Value=168000000
RCC.APB1CLKDivider=RCC_HCLK_DIV4
RCC.APB1Freq_Value=42000000
RCC.APB1TimFreq_Value=84000000
RCC.APB2CLKDivider=RCC_HCLK_DIV2
RCC.APB2Freq_Value=84000000
RCC.APB2TimFreq_Value=168000000
RCC.CortexFreq_Value=168000000
RCC.EthernetFreq_Value=168000000
RCC.FCLKCortexFreq_Value=168000000
RCC.FamilyName=M
RCC.HCLKFreq_Value=168000000
RCC.HSE_VALUE=16000000
RCC.HSI_VALUE=16000000
RCC.I2SClocksFreq_Value=192000000
RCC.IPParameters=48MHZClocksFreq_Value,AHBFreq_Value,APB1CLKDivider,APB1Freq_Value,APB1TimFreq_Value,APB2CLKDivider,APB2Freq_Value,APB2TimFreq_Value,CortexFreq_Value,EthernetFreq_Value,FCLKCortexFreq_Value,FamilyName,HCLKFreq_Value,HSE_VALUE,HSI_VALUE,I2SClocksFreq_Value,LSE_VALUE,LSI_VALUE,MCO2PinFreq_Value,PLLCLKFreq_Value,PLLM,PLLN,PLLQ,PLLQCLKFreq_Value,RTCFreq_Value,RTCHSEDivFreq_Value,SYSCLKFreq_VALUE,SYSCLKSource,VCOI2SOutputFreq_Value,VCOInputFreq_Value,VCOOutputFreq_Value,VcooutputI2S
RCC.LSE_VALUE=32768
RCC.LSI_VALUE=32000
RCC.MCO2PinFreq_Value=168000000
RCC.PLLCLKFreq_Value=168000000
RCC.PLLM=8
RCC.PLLN=168
RCC.PLLQ=7
RCC.PLLQCLKFreq_Value=48000000
RCC.RTCFreq_Value=32000
RCC.RTCHSEDivFreq_Value=8000000
RCC.SYSCLKFreq_VALUE=168000000
RCC.SYSCLKSource=RCC_SYSCLKSOURCE_PLLCLK
RCC.VCOI2SOutputFreq_Value=384000000
RCC.VCOInputFreq_Value=2000000
RCC.VCOOutputFreq_Value=336000000
RCC.VcooutputI2S=192000000
SDIO.ClockBypass=SDIO_CLOCK_BYPASS_DISABLE
SDIO.ClockDiv=0
SDIO.IPParameters=ClockDiv,ClockBypass
SH.GPXTI0.0=GPIO_EXTI0
SH.GPXTI0.ConfNb=1
SH.GPXTI12.0=GPIO_EXTI12
SH.GPXTI12.ConfNb=1
SH.GPXTI15.0=GPIO_EXTI15
SH.GPXTI15.ConfNb=1
SH.GPXTI3.0=GPIO_EXTI3
SH.GPXTI3.ConfNb=1
SH.GPXTI4.0=GPIO_EXTI4
SH.GPXTI4.ConfNb=1
SH.GPXTI5.0=GPIO_EXTI5
SH.GPXTI5.ConfNb=1
SPI1.BaudRatePrescaler=SPI_BAUDRATEPRESCALER_8
SPI1.CalculateBaudRate=10.5 MBits/s
SPI1.Direction=SPI_DIRECTION_2LINES
SPI1.IPParameters=VirtualType,Mode,Direction,CalculateBaudRate,BaudRatePrescaler
SPI1.Mode=SPI_MODE_MASTER
SPI1.VirtualType=VM_MASTER
SPI2.BaudRatePrescaler=SPI_BAUDRATEPRESCALER_4
SPI2.CalculateBaudRate=10.5 MBits/s
SPI2.Direction=SPI_DIRECTION_2LINES
SPI2.IPParameters=VirtualType,Mode,Direction,CalculateBaudRate,BaudRatePrescaler
SPI2.Mode=SPI_MODE_MASTER
SPI2.VirtualType=VM_MASTER
TIM2.IPParameters=Prescaler
TIM2.Prescaler=83
TIM3.IPParameters=Period
TIM3.Period=840-1
USB_OTG_FS.IPParameters=VirtualMode
USB_OTG_FS.VirtualMode=Device_Only
VP_FATFS_VS_SDIO.Mode=SDIO
VP_FATFS_VS_SDIO.Signal=FATFS_VS_SDIO
VP_SYS_VS_Systick.Mode=SysTick
VP_SYS_VS_Systick.Signal=SYS_VS_Systick
VP_TIM2_VS_ClockSourceINT.Mode=Internal
VP_TIM2_VS_ClockSourceINT.Signal=TIM2_VS_ClockSourceINT
VP_TIM3_VS_ClockSourceINT.Mode=Internal
VP_TIM3_VS_ClockSourceINT.Signal=TIM3_VS_ClockSourceINT
board=custom
isbadioc=false

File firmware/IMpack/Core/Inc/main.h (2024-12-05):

/* USER CODE BEGIN Header */
/**
  ******************************************************************************
  * @file           : main.h
  * @brief          : Header for main.c file.
  *                   This file contains the common defines of the application.
  ******************************************************************************
  * @attention
  *
  * Copyright (c) 2024 STMicroelectronics.
  * All rights reserved.
  *
  * This software is licensed under terms that can be found in the LICENSE file
  * in the root directory of this software component.
  * If no LICENSE file comes with this software, it is provided AS-IS.
  *
  ******************************************************************************
  */
/* USER CODE END Header */

/* Define to prevent recursive inclusion -------------------------------------*/
#ifndef __MAIN_H
#define __MAIN_H

#ifdef __cplusplus
extern "C" {
#endif

/* Includes ------------------------------------------------------------------*/
#include "stm32f4xx_hal.h"

/* Private includes ----------------------------------------------------------*/
/* USER CODE BEGIN Includes */

/* USER CODE END Includes */

/* Exported types ------------------------------------------------------------*/
/* USER CODE BEGIN ET */

/* USER CODE END ET */

/* Exported constants --------------------------------------------------------*/
/* USER CODE BEGIN EC */

/* USER CODE END EC */

/* Exported macro ------------------------------------------------------------*/
/* USER CODE BEGIN EM */

/* USER CODE END EM */

/* Exported functions prototypes ---------------------------------------------*/
void Error_Handler(void);

/* USER CODE BEGIN EFP */

/* USER CODE END EFP */

/* Private defines -----------------------------------------------------------*/
#define ADXL37x_INT2_Pin GPIO_PIN_0
#define ADXL37x_INT2_GPIO_Port GPIOA
#define ADXL37x_NSS_Pin GPIO_PIN_1
#define ADXL37x_NSS_GPIO_Port GPIOA
#define IIS3DWB_INT2_Pin GPIO_PIN_3
#define IIS3DWB_INT2_GPIO_Port GPIOA
#define SPI1_NSS_Pin GPIO_PIN_4
#define SPI1_NSS_GPIO_Port GPIOA
#define ADXL37x_INT1_Pin GPIO_PIN_4
#define ADXL37x_INT1_GPIO_Port GPIOC
#define ADXL37x_INT1_EXTI_IRQn EXTI4_IRQn
#define LSM6DSx_INT2_Pin GPIO_PIN_5
#define LSM6DSx_INT2_GPIO_Port GPIOC
#define LSM6DSx_INT2_EXTI_IRQn EXTI9_5_IRQn
#define LSM6DSx_INT1_Pin GPIO_PIN_12
#define LSM6DSx_INT1_GPIO_Port GPIOB
#define LSM6DSx_INT1_EXTI_IRQn EXTI15_10_IRQn
#define IIS3DWB_NSS_Pin GPIO_PIN_14
#define IIS3DWB_NSS_GPIO_Port GPIOB
#define IIS3DWB_INT1_Pin GPIO_PIN_15
#define IIS3DWB_INT1_GPIO_Port GPIOB
#define IIS3DWB_INT1_EXTI_IRQn EXTI15_10_IRQn
#define LED_STATUS_Pin GPIO_PIN_9
#define LED_STATUS_GPIO_Port GPIOA
#define SD_CARD_DETECT_Pin GPIO_PIN_10
#define SD_CARD_DETECT_GPIO_Port GPIOA
#define BUTTON_Pin GPIO_PIN_4
#define BUTTON_GPIO_Port GPIOB

/* USER CODE BEGIN Private defines */

/* USER CODE END Private defines */

#ifdef __cplusplus
}
#endif

#endif /* __MAIN_H */

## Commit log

2024-12-05 added board files
    [IMpack.kicad_pcb, IMpack.kicad_sch, Microcontroller.kicad_sch, Miscellaneous.kicad_sch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]
2024-12-05 added board production files
    [BOM-IMpack.csv, CPL-IMpack.csv, IMpack-CuBottom.gbr, IMpack-CuIn1.gbr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]
2025-03-07 added mechanical designs
    [IMpack shaker mount.f3z, IMpack shaker mount.step, IMpack threaded mount.f3d, IMpack threaded mount.step]
